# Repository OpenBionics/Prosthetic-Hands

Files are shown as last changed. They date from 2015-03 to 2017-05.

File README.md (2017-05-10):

# OpenBionics - Prosthetic Hands
 
Nowadays most prosthetic hands cost dozens of thousands of USD. The OpenBionics initiative (www.openbionics.org) presents a new open-source design for highly functional prosthetic hands. The proposed hands cost less than 200$, weigh less than 300 gr and can be easily fabricated with off-the-shelf materials and rapid prototyping techniques (3D Printing). 

A novel differential mechanism (based on the whiffletree) allows the user to block the motion of each finger independently and facilitates the execution of 144 different grasps with only 1 actuator. The design is based on parametric models of hand anthropometry studies, so it can easily be personalized to specific patients.

## Contents

In this repository you can find:
* Detailed assembly guide for the replication of OpenBionics prosthetic hand 
* Parametric CAD files for personalized design
  * 2D CAD design files for laser cutter 
  * 3D CAD design files for 3D printer
* Breakout board 
* Prosthetic hand kinematics in MATLAB using robotics toolbox
* Arduino software for HerkuleX DRS-0201 servo motor operation
* Archive of various images

## Notes

Please open a [GitHub issue](https://github.com/OpenBionics/Prosthetic-Hands/issues) if you encounter any problem.

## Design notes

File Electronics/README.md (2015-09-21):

# Electronic Breakout Board for Prosthetic Hand

We present the development of a breakout board for controlling our prosthetic hand. It is a PCB (printed circuit board) with pin headers to accomodate two different servo motors, such as standard servo and herkulex. It can have both analog inputs (e.g. [EMG](http://www.advancertechnologies.com/p/muscle-sensor-v3.html) signals) and digital inputs (e.g. buttons for [RobotHandExtension](https://github.com/OpenBionics/Robot-Hands/tree/master/CAD/Interfaces/Extension)).
An I2C bus can also be used in order to connect sensors like [takktile] (http://www.takktile.com/) or other servos such as the [openservo](http://openservo.com/). The breakout board also has external pins for development. 

The main microcontroller we currently use is an Arduino Micro Pro, equipped with an ATmega32U4 core. The PCB can be powered by an external power supply or a battery. 

The board is currently under testing. Pictures of the board and its development process can be found below.

# Pinout

The Pin Mapping of the breakout board.

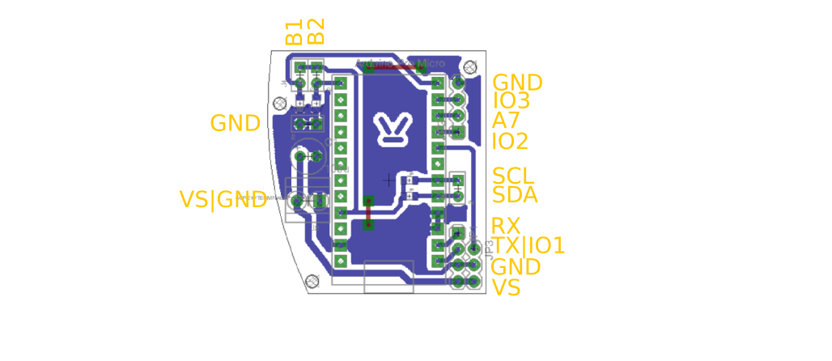
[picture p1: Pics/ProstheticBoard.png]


# Board Development

The development of the breakout board was done using the facilities of
the Athens Hackerspace (Thanks!!!). Some photos of the development process and 
final result.

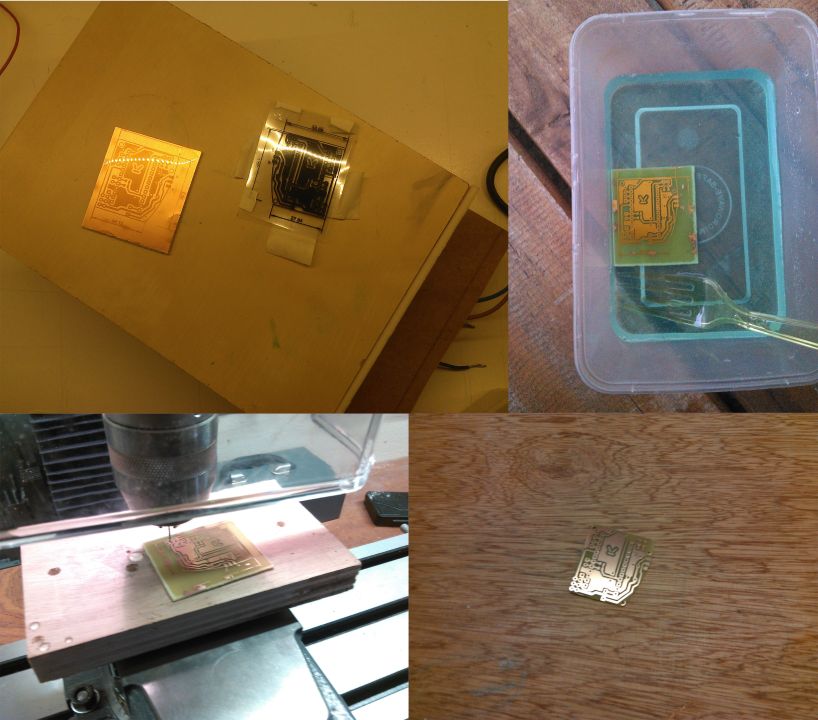
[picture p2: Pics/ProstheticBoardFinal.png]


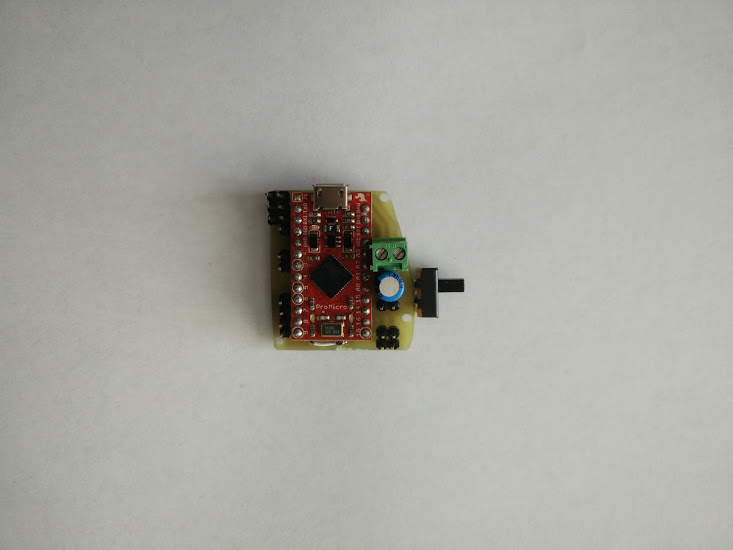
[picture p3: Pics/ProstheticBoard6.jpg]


The OpenBionics Electronics Library can be found [here](https://github.com/OpenBionics/Robot-Hands/tree/master/Electronics).

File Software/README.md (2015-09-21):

# Arduino Firmware

In order to evaluate the capabilities of our prosthetic hand, we developed a simple firmware for Arduino using this [library](http://robottini.altervista.org/dongbu-herkulex-arduino-library-2) for Herkulex DRS-0201. 

We modified the library in order to control the motor with an [Arduino](https://www.arduino.cc) Micro Pro.

# Next Steps

We plan on controlling our prosthetic hands with different interfaces, such as [these](https://github.com/OpenBionics/Robot-Hands/tree/master/CAD/Interfaces) or EMG sensors. 

A schematic depicting the high-level control architecture of our prosthetic hands can be found below.

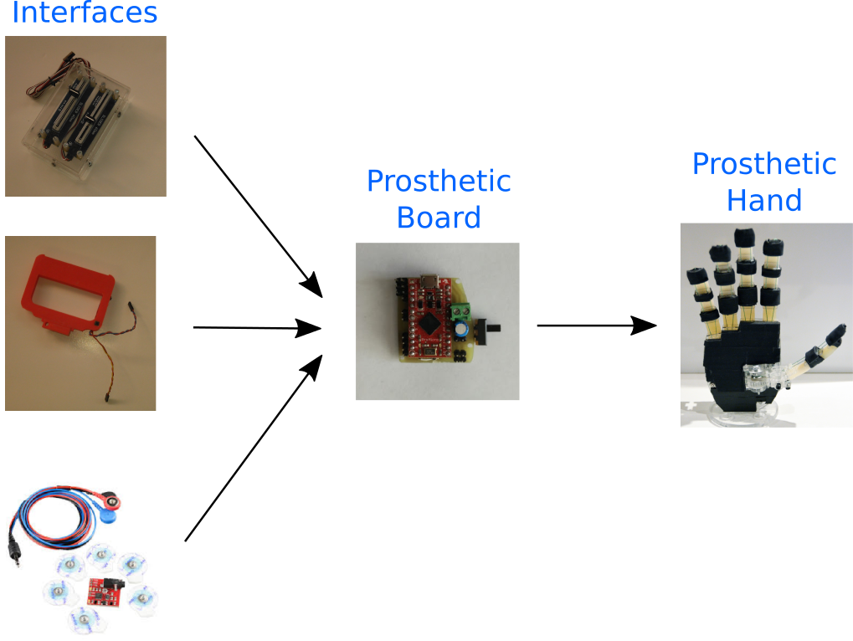
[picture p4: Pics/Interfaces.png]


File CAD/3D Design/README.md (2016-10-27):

# Parametric CAD file for 2D Design

## Guide for personalized design

Τhe use of parametric models derived from human hand anthropometry studies, allows for the development of personalized prostheses. The only parameters that we need in order to derive the finger phalanges lengths and the personalized finger base frames positions and orientations, are the human hand length (HL) and the human hand breadth (HB). 

We have modified our CAD files in order to integrate the required parameters (HL & HB) for the replication of a personalized design. Firstly, you need to decide which hand you want to replicate (Right or Left). You can find below a quick guide for the production of the personalized design. The procedure is the same for both hands.

1. Open the part file "prostheticParameters.SLDPRT" which can be found @ <a href="https://github.com/OpenBionics/Prosthetic-Hands/blob/master/CAD/3D%20Design/Left_hand/prostheticParameters.SLDPRT">Prosthetic-Hands/CAD/3D Design/Left_hand</a>.
2. Make the "parametersSketch" file editable. You can see there, the parameters that you can change. Their values are reported in mm and NOT in inches.
3. Open the assembly file "AnthropomorphicHandAssembly.SLDASM" which can be found @ <a href= "https://github.com/OpenBionics/Prosthetic-Hands/tree/master/CAD/3D%20Design/Left_hand/Assembly">Prosthetic-Hands/CAD/3D Design//Left_hand/Assembly</a>.
4. Go to the file "prostheticParameters.SLDPRT" and change the desired values (HL=hand length, HB=hand breadth & fingerWidth) according to the following figure and then save the file.

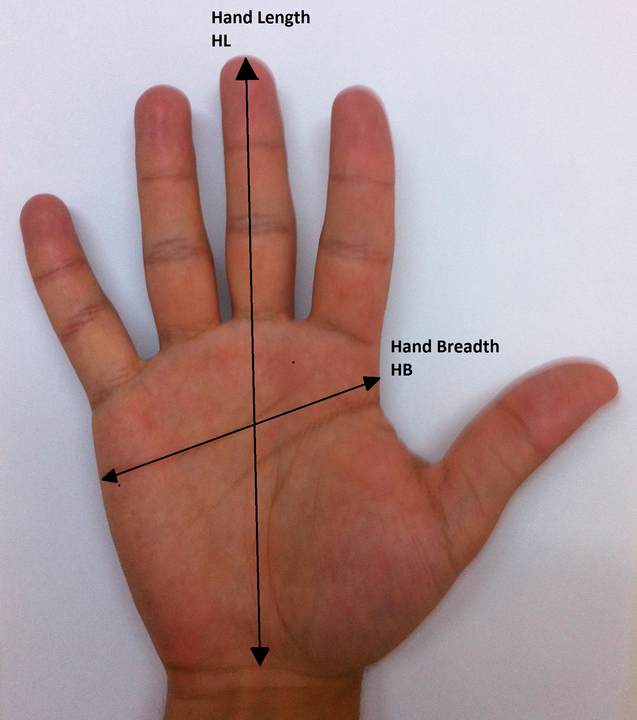
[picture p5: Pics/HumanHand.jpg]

 
5. Go to the assembly file "AnthropomorphicHandAssembly.SLDASM" and rebuild it. All .SLDPRT files that are used in the assembly should be rebuilt.
6. If you want .STL files, you should open every rebuilt part and then choose "Save as .STL".

## 3D Design Model

In the following figure you can see the 2D Design model

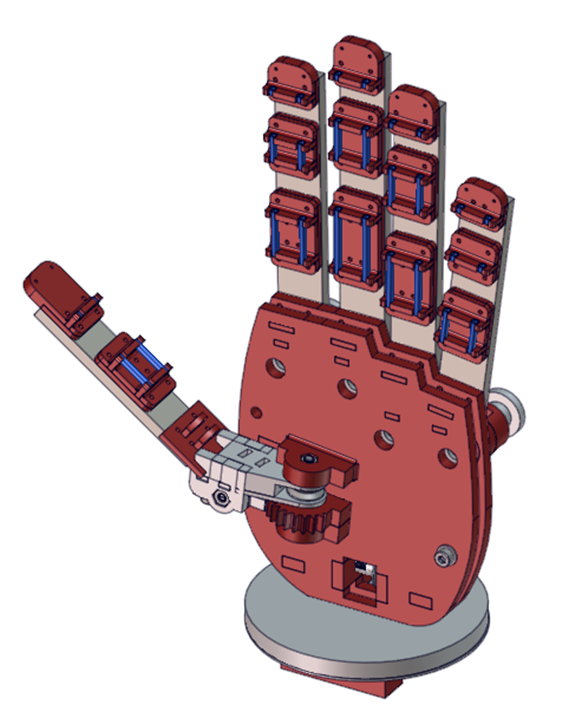
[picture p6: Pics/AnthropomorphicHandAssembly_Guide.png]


##Things to note:

1. The design has specific constraints, which cover the 95th percentile of the human hand and those are:<br/>
Hand Length: 182 - 225 mm<br/>
Hand Breadth: 82.5 - 110 mm.
2. Dimensions should be changed symmetrically. The mean HL/HB ratio is 2.2, so if your new assembly has errors it is probably either because you didn't measure correctly your hand values or because your hand construction is very far from the human mean value. 
3. For editing our CAD files you should own Solidworks 2014 or a later version. In case that you don't have the required software, complete this <a href="http://www.openbionics.org/personalizeddesignswebform/">webform</a> in the <a href="http://www.openbionics.org/">OpenBionics</a> website. We are currently in the process of preparing our designs with open-source CAD software. 
4. Our approach is inspired by the Yale Open Hand project. More details can be found <a href="http://www.eng.yale.edu/grablab/openhand/OpenHand%20CAD%20Guide.pdf">here<a/>.

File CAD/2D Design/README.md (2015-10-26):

# Parametric CAD file for 2D Design

## Guide for perosnaliszd design

Τhe use of parametric models derived from human hand anthropometry studies, allows for the development of personalized prostheses. The only parameters that we need in order to derive the finger phalanges lengths and the personalized finger base frames positions and orientations, are the human hand length (HL) and the human hand breadth (HB). 

We have modified our CAD files in order to integrate the required parameters (HL & HB) for the replication of a personalized design. Firstly, you need to decide which hand you want to replicate (Right or Left). You can find below a quick guide for the production of the personalized design. The procedure is the same for both hands.

1. Open the part file "prostheticParameters.SLDPRT" which can be found @ <a href="https://github.com/OpenBionics/Prosthetic-Hands/tree/master/CAD/2D%20Design/LeftHand">Prosthetic-Hands/CAD/2D Design/Left</a>.
2. Make the "parametersSketch" file editable. You can see there, the parameters that you can change. Their values are reported in mm and NOT in inches.
3. Open the assembly file "AnthropomorphicHandAssembly.SLDASM" which can be found @ <a href= "https://github.com/OpenBionics/Prosthetic-Hands/tree/master/CAD/2D%20Design/LeftHand/Assembly">Prosthetic-Hands/CAD/2D Design/Left/Assembly</a>.
4. Go to the file "prostheticParameters.SLDPRT" and change the desired values (HL=hand length, HB=hand breadth & fingerWidth) according to the following figure and then save the file.


 
5. Go to the assembly file "AnthropomorphicHandAssembly.SLDASM" and rebuild it. All .SLDPRT files that are used in the assembly should be rebuilt.
6. If you want .STL files, you should open every rebuilt part and then choose "Save as .STL".

## 2D Design Model

In the following figure you can see the 2D Design model

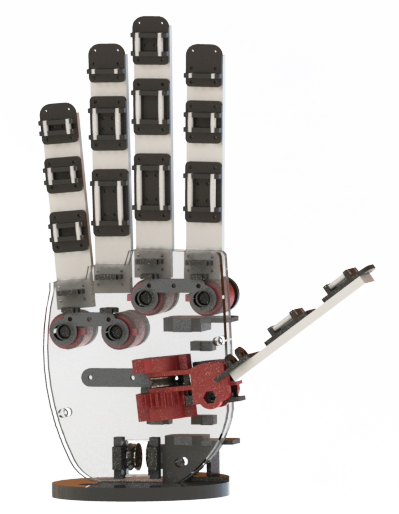
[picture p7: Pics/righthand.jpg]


## Things to note:

1. The design has specific constraints, which cover the 95th percentile of the human hand and those are:<br/>
Hand Length: 182 - 225 mm<br/>
Hand Breadth: 82.5 - 110 mm.
2. Dimensions should be changed symmetrically. The mean HL/HB ratio is 2.2, so if your new assembly has errors it is probably either because you didn't measure correctly your hand values or because your hand construction is very far from the human mean value. 
3. For editing our CAD files you should own Solidworks 2014 or a later version. In case that you don't have the required software, complete this <a href="http://www.openbionics.org/personalizeddesignswebform/">webform</a> in the <a href="http://www.openbionics.org/">OpenBionics</a> website. We are currently in the process of preparing our designs with open-source CAD software. 
4. Our approach is inspired by the Yale Open Hand project. More details can be found <a href="http://www.eng.yale.edu/grablab/openhand/OpenHand%20CAD%20Guide.pdf">here<a/>.

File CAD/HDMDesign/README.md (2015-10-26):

# New HDM Design of Robot Fingers

## Introduction

Our initial method of creating fingers for robot and prosthetic hands was very simple and it didn't require any complex tools (silicone sheets were stitched onto the rigid phalanges with simple needles). The main disadvantages of this method are:
* the process isn't automated,
* the aesthetic aspect of the finger is not optimal (i.e., it doesn't feel like a product),
* the finger cannot easily accommodate extra parts (e.g., sensing elements or other electronics).

For these reasons we searched different fabrication methods for developing hands based on flexure joints.

Recently Ma et al [1] proposed a new methodology that is called hybrid deposition manufacturing [HDM](http://www.eng.yale.edu/grablab/pubs/Ma_JMR2015.pdf). HDM combines additive manufacturing (AM) with multi-material deposition and embedded components in order to produce robotic, mechatronic, and other articulated mechanisms.

## Design

Using the HDM approach for our prosthetic fingers we can embed inside them a wide range of electronics, like force sensors, flex sensors or even NFC tags that will facilitate interactions with other electronic devices. Of course the new design has the disadvantage that it requires more complex tools and is slightly more expensive.

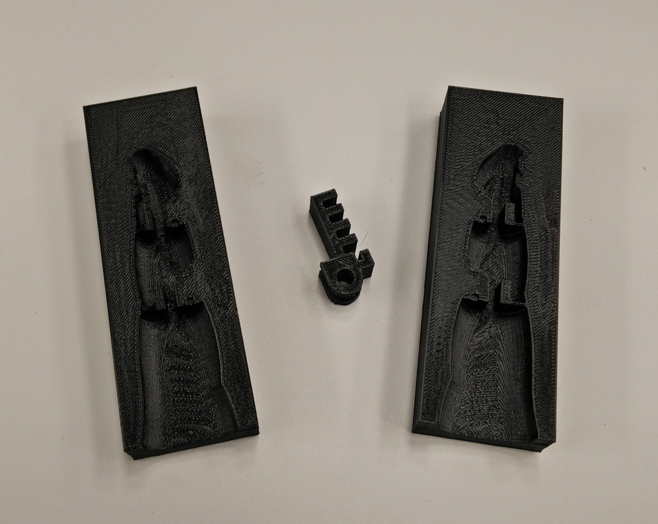
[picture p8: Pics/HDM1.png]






The proposed design can be based on the human hand model. For now we use a ready [model](https://grabcad.com/library/human-left-hand) in SolidWorks. In the future we plan to use a 3D scanner (e.g., kinect, project soli, etc.) to reconstruct the intact hand of amputee, derive the mirror hand and build a personalized prosthesis.

To use this new design in SolidWorks, you can download the files form [here](https://grabcad.com/library/human-left-hand). When you open the .sldASM files, SolidWorks will ask for the missing parts. These parts can be found in the following [3D model](https://grabcad.com/library/human-left-hand). A future direction of ours is to make the HDM design parametric and migrate it to FreeCAD, as we did for the [initial design](https://hackaday.io/project/4745-openbionics-affordable-prosthetic-hands/log/27049-prosthetic-hand-in-freecad-palm-and-tendon-routing).

## Materials and Tools Required

As depicted the build of materials are:

* paint of the desired color
* liquid polyurethane (PMC 780)
* cotton swabs
* paper tape
* NFC tags

The necessary tools are:

* a weighting scale
* a vacuum chamber
* plastic cups to mix the two liquid silicone parts.

The prices of the different hand components can be found [here](https://hackaday.io/project/4745-openbionics-affordable-prosthetic-hands/log/27133-the-role-of-the-openbionics-project-in-a-world-of-overprized-prosthetic-devices). The NFC tags [cost](http://www.amazon.com/gp/product/B00MNYCIKG?psc=1&redirect=true&ref_=oh_aui_detailpage_o00_s00) 15.50$ (for 25 tags). 



## More Details

More details about this design can be found [here](https://hackaday.io/project/4745/logs?page=2).

### References

[1] Raymond R. Ma, Joseph T. Belter and Aaron M. Dollar, "Hybrid Deposition Manufacturing: Design Strategies for Multi-Material Mechanisms via 3D-Printing and Material Deposition", Journal of Mechanisms and Robotics, 2015.

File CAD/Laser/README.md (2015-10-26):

# Laser Cutter files

These files should be imported to a laser cutter to build the 2D Design Hand.

## Building

For the version created with the laser cutter, we used Plexiglas (acrylic) because it is low-cost, light-weight, it can be easily found, it has good durability, significant ultimate tensile strength (8.500 - 11.250 psi) and almost the same density (1.19 gr / cubic cm | 0.043 lbs / cubic inch), with other common plastics like ABS. The laser cutting machine used, was the Universal Laser Systems VSL 3.5 that appears in the following image. The estimated fabrication time with the laser cutter is ~ 2 hrs.

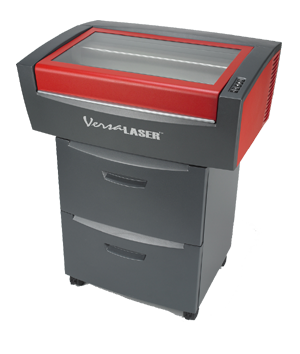
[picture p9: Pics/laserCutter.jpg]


The Prosthetic Hand with laser cutting parts appears in the following image.

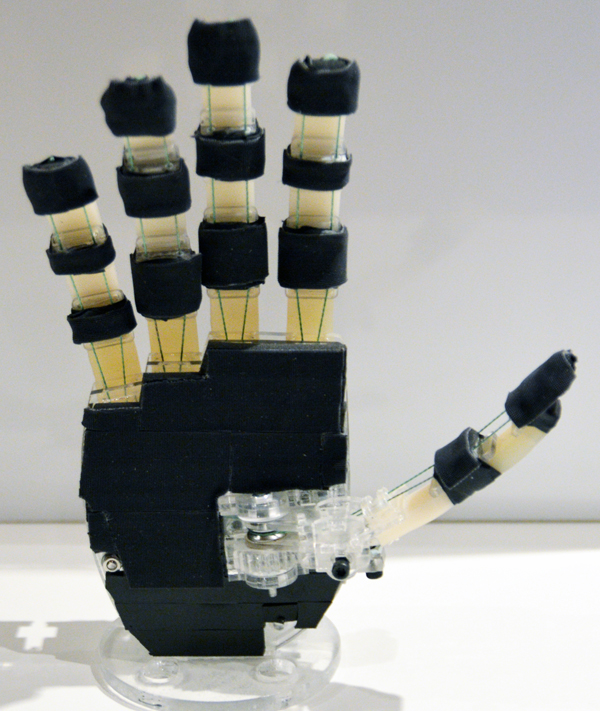
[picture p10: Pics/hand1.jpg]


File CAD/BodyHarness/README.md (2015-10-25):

# Α Body Powered Actuation System for Prosthetic Hands

## The Idea

An old and reliable method of controlling prosthetic devices is by using a harness-socket actuation system in a body powered manner [1]. In order to further reduce the cost of our prosthetic hands omitting any kind of electronics and servos, we designed a body powered actuation system that an amputee can use as an interface to control a prosthetic hand. The proposed system is inspired by the classic harness-socket actuation systems but is designed as an exosceleton. The system consists of modular parts. Depending on the user's arm length an appropriate number of intermediate modules can be printed together with the end-effector and the tendon routing entry part.

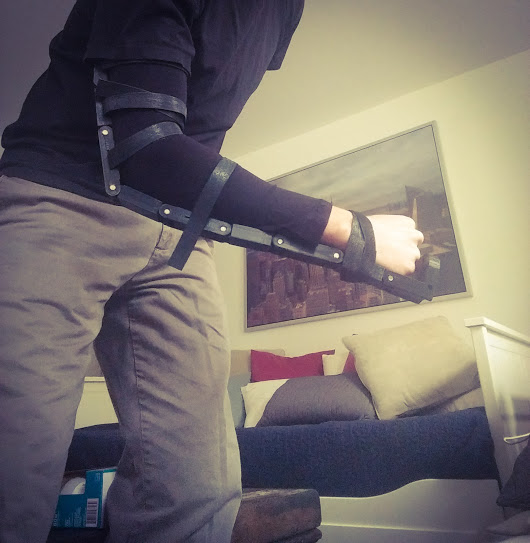
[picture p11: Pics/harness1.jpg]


## Description

The proposed body powered actuation system, consists of:
* modular 3D-printed parts 
* pins, dowels or shafts
* velcro tape
* an elastic arm sleeve
* dyneema thread

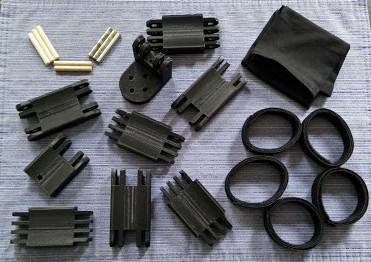
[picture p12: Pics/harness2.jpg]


The mechanism can be replicated and assembled quite easily, as depicted in the picture below. Moreover, the proposed system with a prosthetic hand attached at the end-effector, can be used as a body powered prosthesis simulator for non-amputees that want to experience how functional a prosthesis is (e.g., kin that want to experience what amputees - family members feel). The cost of the system is less than 25$ and the weight 250 gr. Enjoy! 

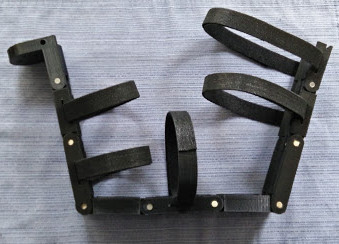
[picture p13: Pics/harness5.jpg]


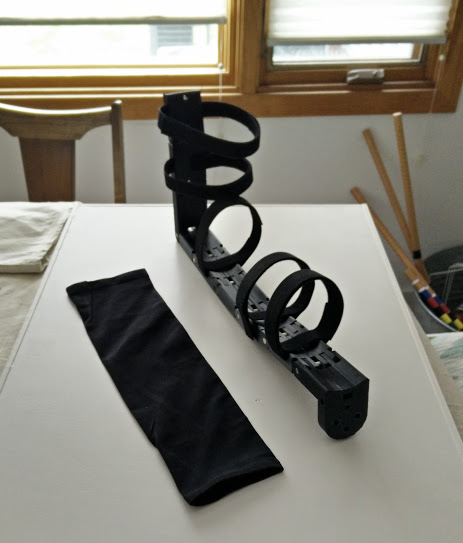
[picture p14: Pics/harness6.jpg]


**References:** 

[1] R. J. Pursley, "Harness patterns for upper-extremity prostheses", Artif Limbs, 2(3):26-60, Sep 1955.

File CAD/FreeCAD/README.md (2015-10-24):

# Prosthetic Hand in Freecad

As we have already mentioned [here](https://hackaday.io/project/4745-openbionics-affordable-prosthetic-hands/log/25696-migrating-our-designs-to-freecad), we are in the process of migrating our designs to Freecad in order to be freely accessible to all and because we believe in fully open source solutions!

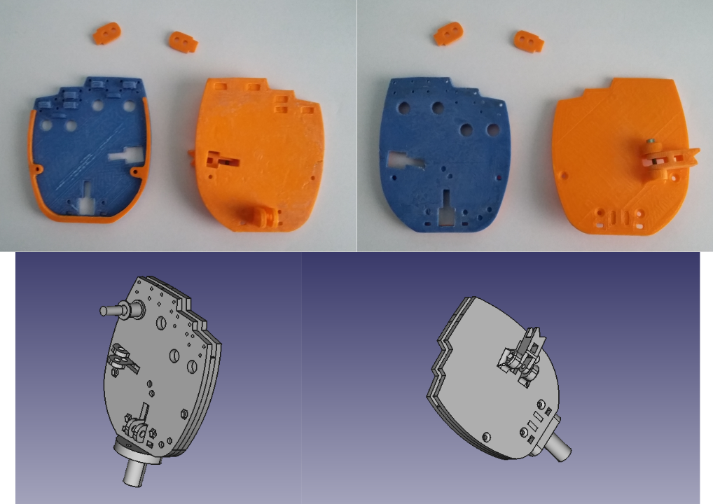
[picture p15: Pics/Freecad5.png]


Up to now we have designed the palm with the differential and the thumb abduction / adduction mechanisms. Prosthetic fingers (the easy part) will follow as we are in the process of improving their design. We have also redesigned some parts for better performance (e.g., the bars of the differential mechanism are changed).

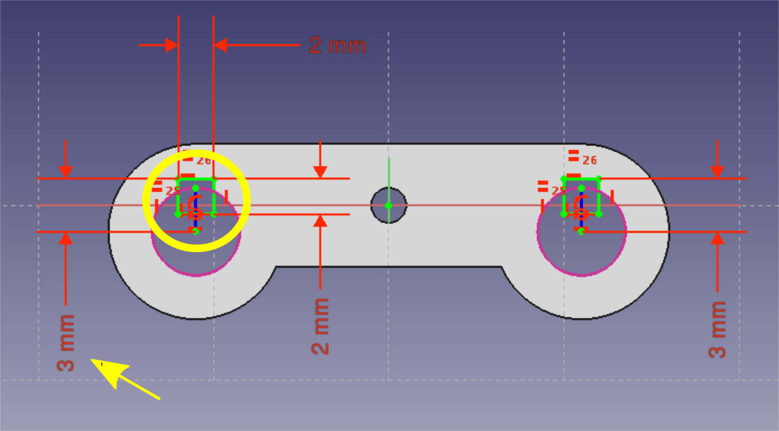
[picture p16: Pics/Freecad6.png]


As depicted, we reduced the radius of the button axle and the radius of the holes of the bars. This change, makes the coupled fingers (e.g., index and middle) more independent when one of them is locked. The radius is now 3mm. When one finger is locked and the other moves, the locked finger tendon will move a distance of 3 mm*angle_of_bar. For example, if the angle_of_bar = PI/4 then the tendon moves a distance of ~2.35 mm. 

We also modified the tendon routing. As you can see in the picture below the tendon comes out from the side of palm in order to be connected with the body harness for body powered prosthetic hands. With this configuration you can also put the servo motor in the same position (currently under development).

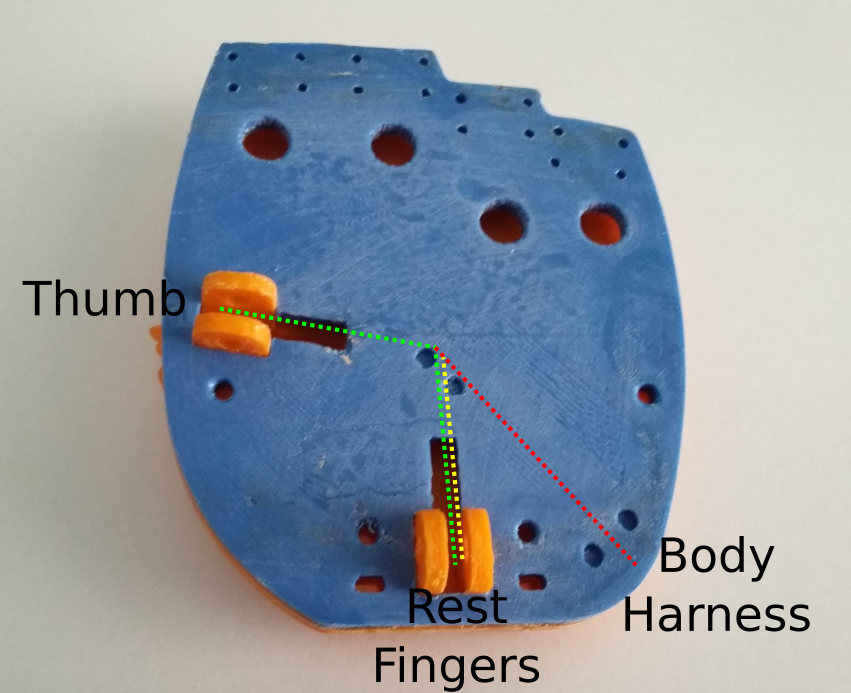
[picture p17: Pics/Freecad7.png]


A new thumb mechanism was also tested. As depicted in the picture below, we tried to add friction with a rubber layer (blue arrow) that needs appropriate tuning in order to resist the force of the tendon.

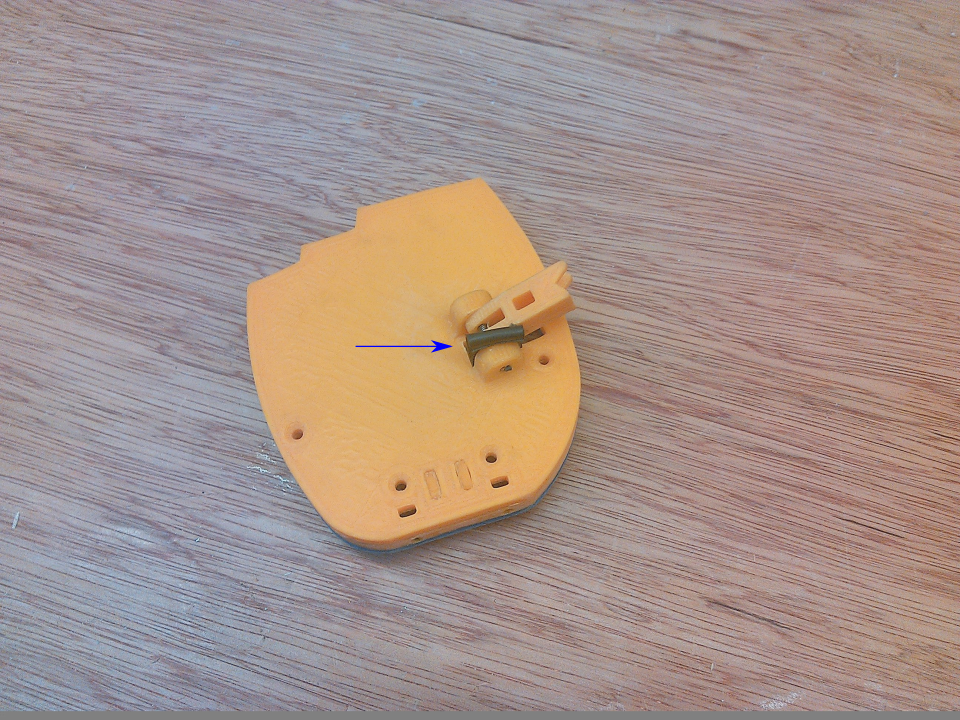
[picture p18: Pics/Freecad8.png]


Stay tuned for more updates!!!

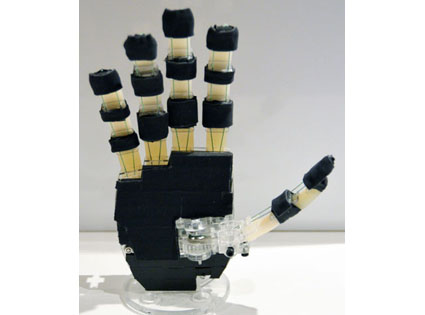
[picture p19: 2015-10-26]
Assembly Guide/tex/figures/paper_images/hand1_small.jpg

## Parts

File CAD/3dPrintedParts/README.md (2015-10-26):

# 3D Printed Parts

These parts should be printed to build the 3D Design Hand.

## Building

For the 3D printed version we used ABS and more precisely red and white 3 mm filaments with the Lulzbot TAZ 4, 3D Printer that appears in the following image. The estimated fabrication time with the 3D printer is ~ 6 hrs.

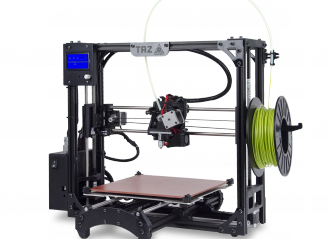
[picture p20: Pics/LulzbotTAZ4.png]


The Prosthetic Hand with 3D printed parts appears in the following image.

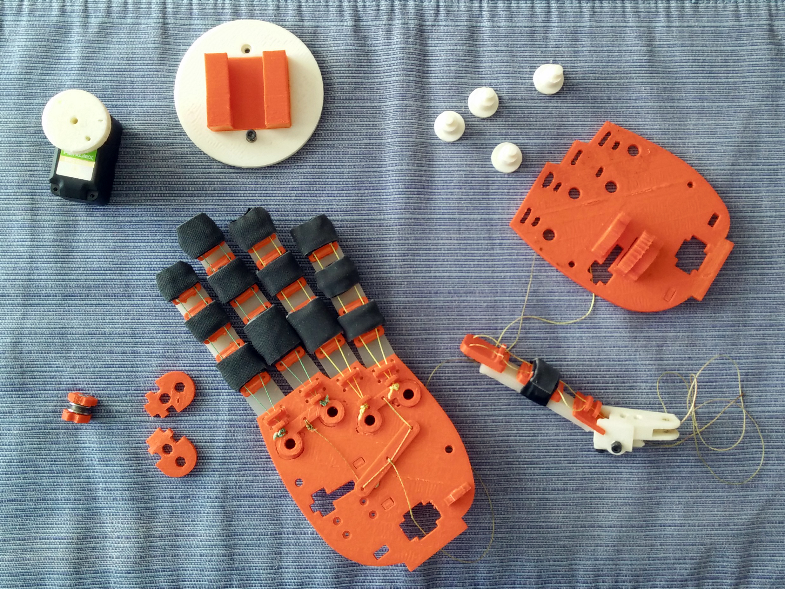
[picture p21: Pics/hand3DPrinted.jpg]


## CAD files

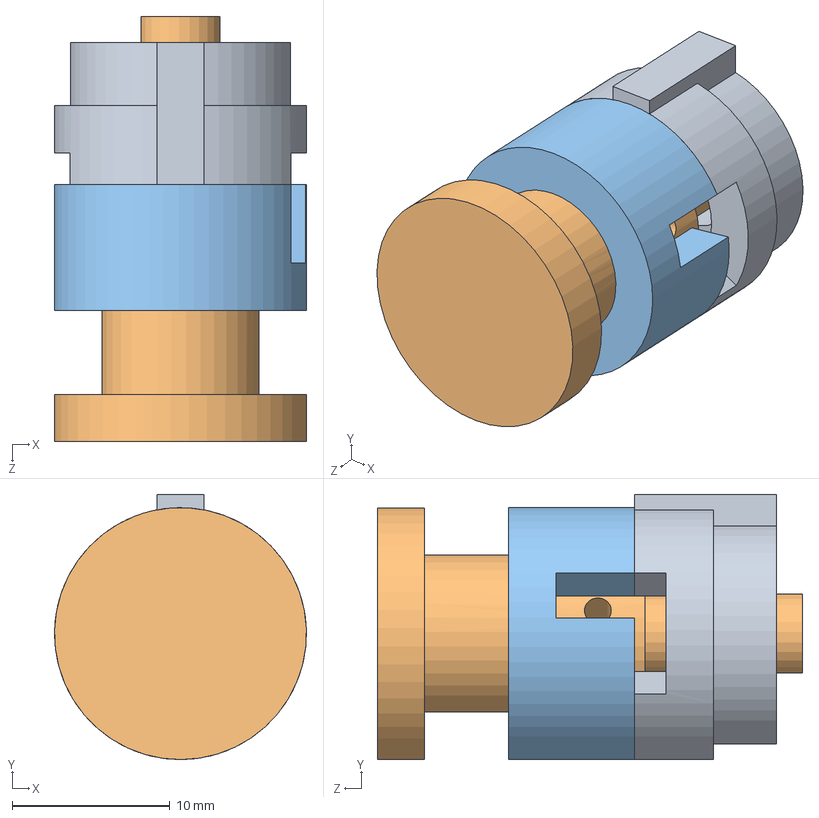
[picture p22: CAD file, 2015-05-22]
CAD/2D Design/LeftHand/Button/src/Button.SLDASM
16.0 x 16.8 x 27.0 mm
buttonBase
buttonAxle
buttonFrame

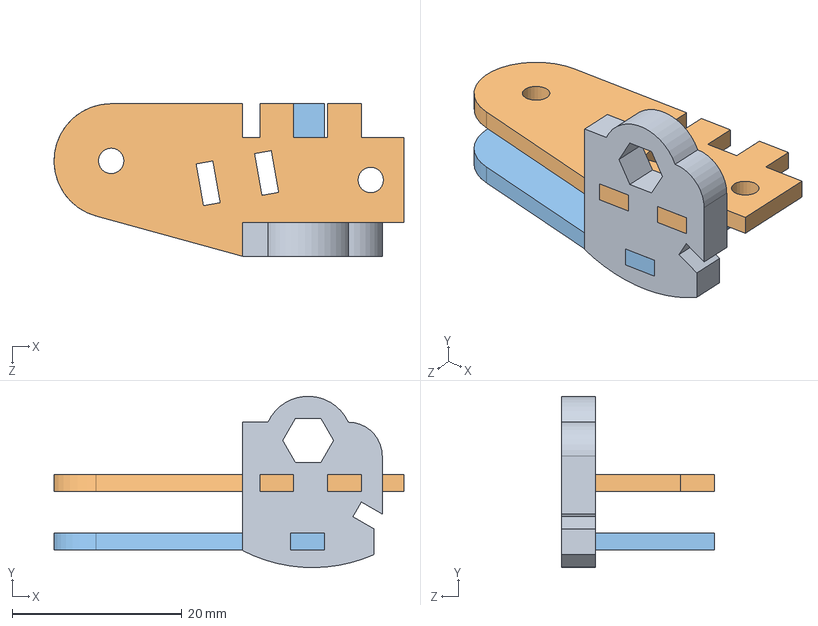
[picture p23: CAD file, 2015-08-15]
CAD/2D Design/LeftHand/Thumb_mechanism/src/thumbMovingMechanism.SLDASM
41.3 x 20.2 x 18.0 mm
thumbMovingBracket
thumbMovingBracketDown
thumbMovingBracketUp

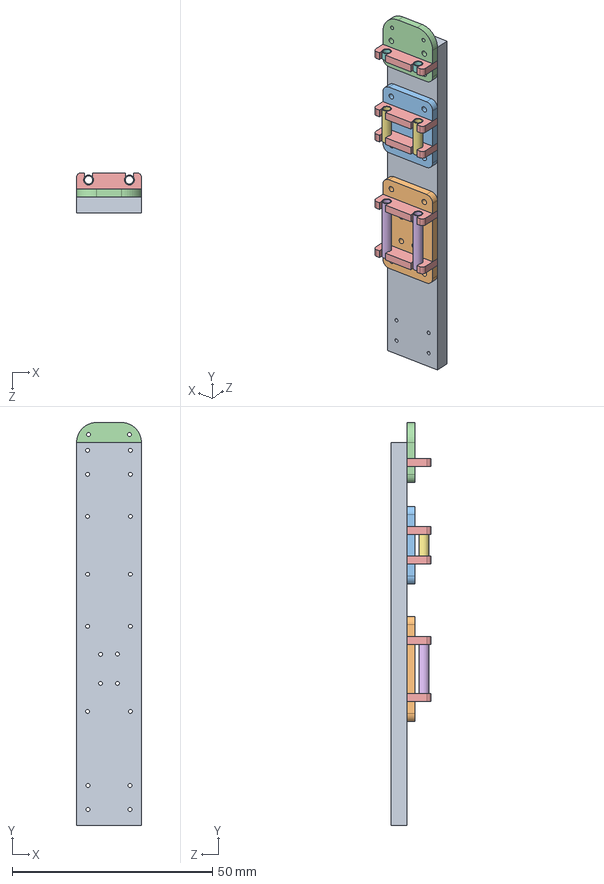
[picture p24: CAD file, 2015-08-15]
CAD/2D Design/RightHand/Fingers/src/Index/index.SLDASM
16.2 x 100.7 x 10.0 mm
indexElastomer
indexPIP
indexMIP
indexDIP
tubeDriver x 5
indexTube1 x 2
indexTube2 x 2
commonFingersTube x 2

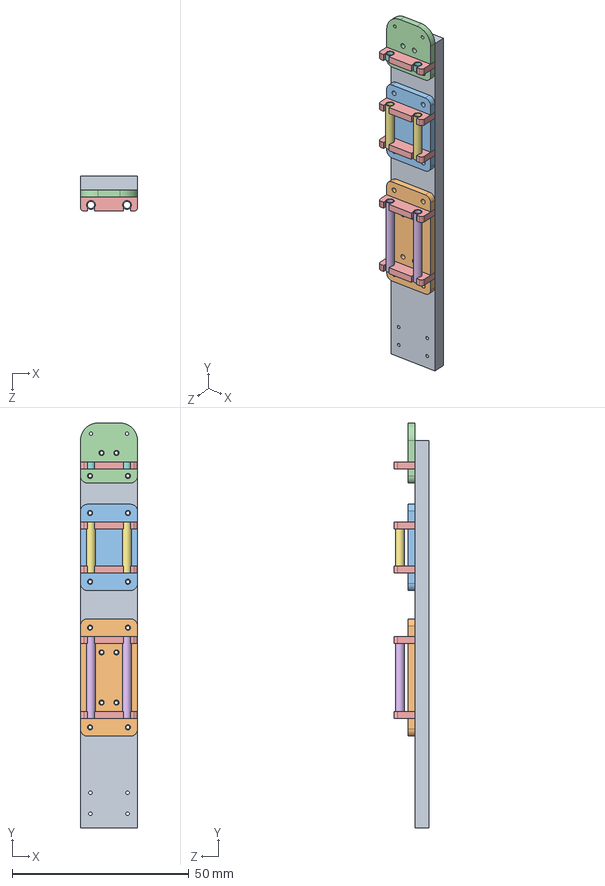
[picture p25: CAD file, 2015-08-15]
CAD/2D Design/RightHand/Fingers/src/Middle/middle.SLDASM
16.2 x 114.6 x 10.0 mm
middleElastomer
middlePIP
middleMIP
middleDIP
tubeDriver x 5
middleTube1 x 2
middleTube2 x 2
commonFingersTube x 2

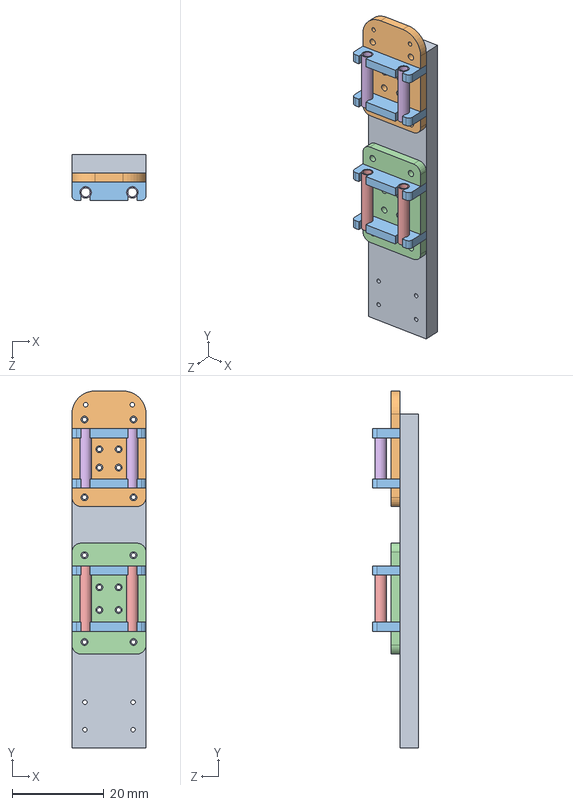
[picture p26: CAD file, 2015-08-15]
CAD/2D Design/RightHand/Fingers/src/Thumb/thumb.SLDASM
16.2 x 78.0 x 10.0 mm
thumbElastomer
thumbDIP
tubeDriver x 4
thumbPIP
thumbTube1 x 2
thumbTube2 x 2

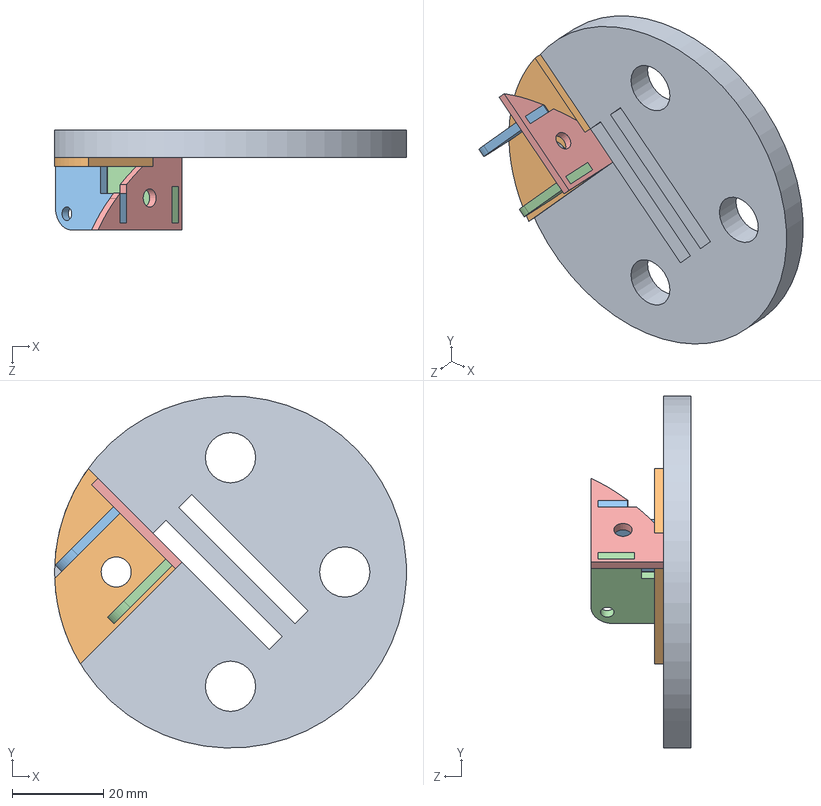
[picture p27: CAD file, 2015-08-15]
CAD/2D Design/RightHand/Flange/src/FlangeAssembly.SLDASM
77.0 x 77.0 x 21.9 mm
flange
supportHandFlange2
SupportBaseFlange1
SupportBaseFlange2
SupportHandFlange1

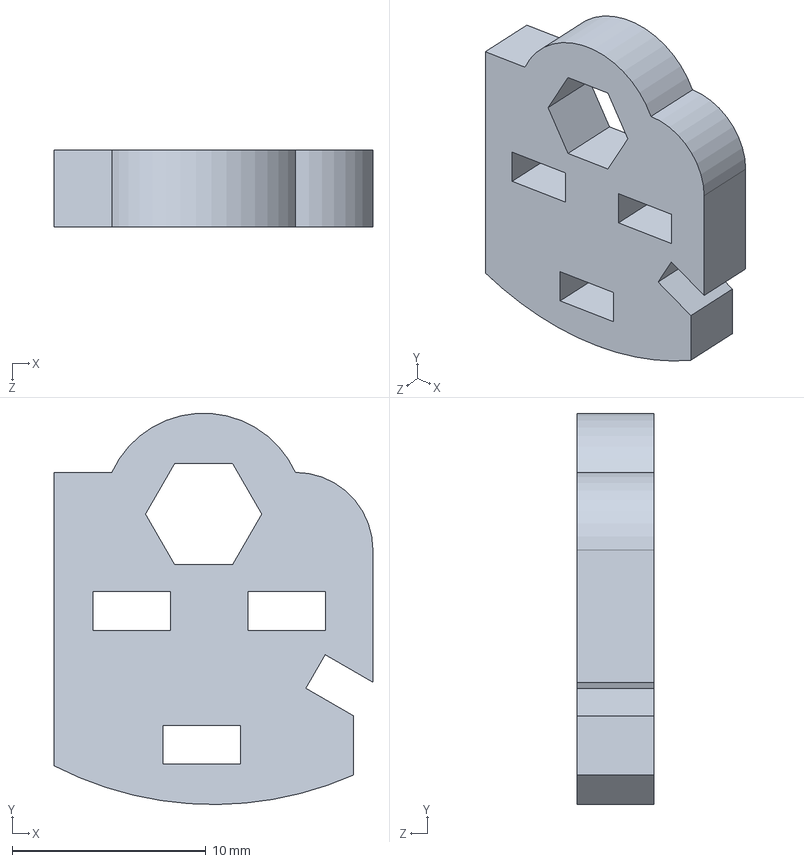
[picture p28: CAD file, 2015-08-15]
CAD/2D Design/RightHand/Thumb_mechanism/src/thumbMovingMechanism.SLDASM
16.5 x 20.2 x 4.00 mm

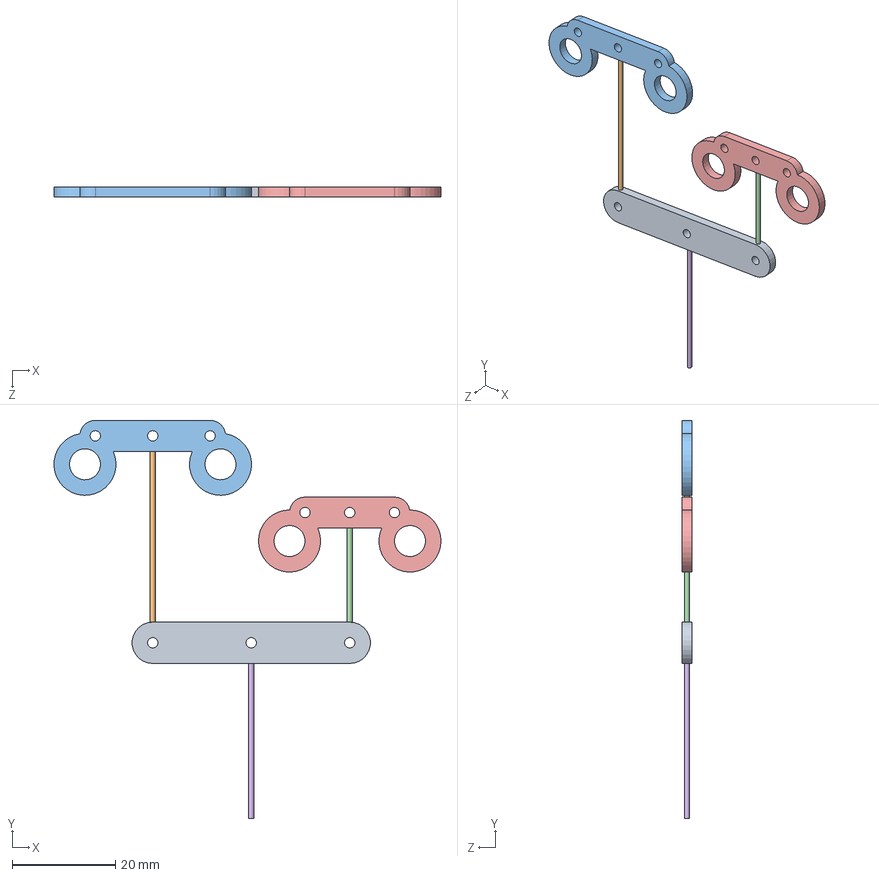
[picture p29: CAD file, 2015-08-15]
CAD/2D Design/RightHand/Whipheel_tree/src/whiffleetree.SLDASM
74.8 x 77.0 x 2.00 mm
mainBar
dynema1
barIndexMiddle
dynema2
barMiddlePinky
dynema3

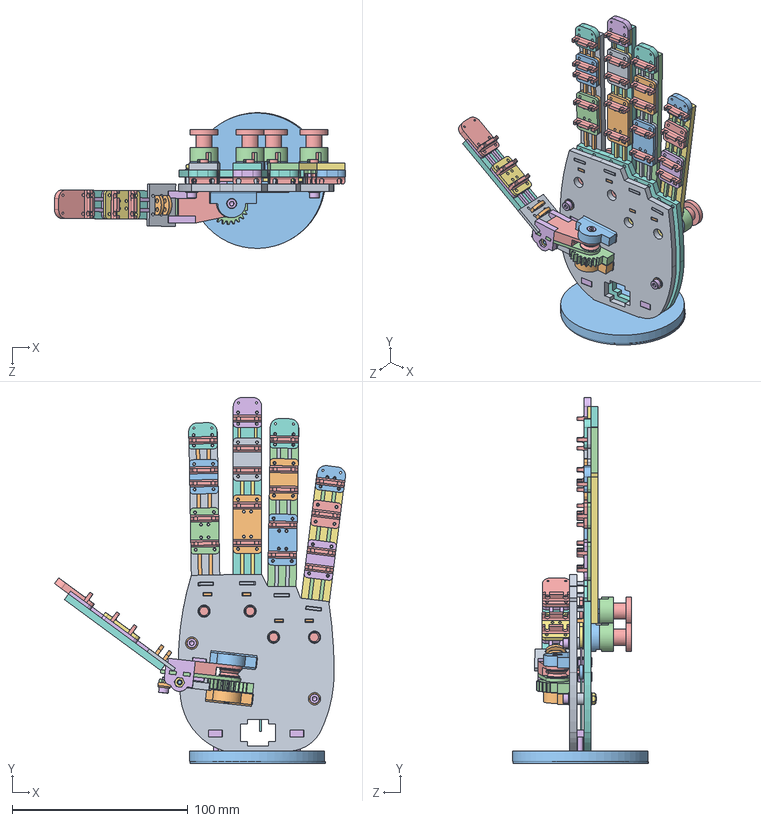
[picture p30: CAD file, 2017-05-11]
CAD/3D Design/Left_hand/Assembly/prostheticLeft.SLDASM
165.5 x 208.2 x 77.2 mm
palmDown
thumbBracket
thumbBracket1
toothedMechansimL
pulley x 2
socket head cap screw_iso x 6
hex nut style 1 gradeab_iso x 5
palmUp
driverBaseFrame1 x 4
driverBaseFrame2 x 4
buttonBase x 4
buttonFrame x 4
buttonAxle x 4
BasePulleyInsidePalm x 4
slotted set screw cup point_iso
indexDIP
indexElastomer
indexJointBase
indexMIP
indexPIP
tubeDriver x 22
middleDIP
middleJointBase
middleElastomer
middleMIP
middlePIP
pinkyDIP
pinkyJointBase
pinkyMIP
pinkyPIP
pinkyElastomer
ringDIP
ringJointBase
ringMIP
ringPIP
ringElastomer
thumbDIP
thumbJointBase
thumbPIP
thumbElastomer
thumbBase
thumbMechanismDriver x 2
mainBar
dynema1
barIndexMiddle
dynema2
barRingPinky
dynema3
spacer x 2
plain washer 10673 type snl_iso x 5
FlangePlate
thumbMovingBracketDown
thumbMovingBracketUp
thumbMovingBracket x 2
lockMechanismBracket x 2
lockMechanismSupport
toothedBlockMechanism
thumbButton
slotted set screw flat point_iso
hex thin nut gradeb_iso

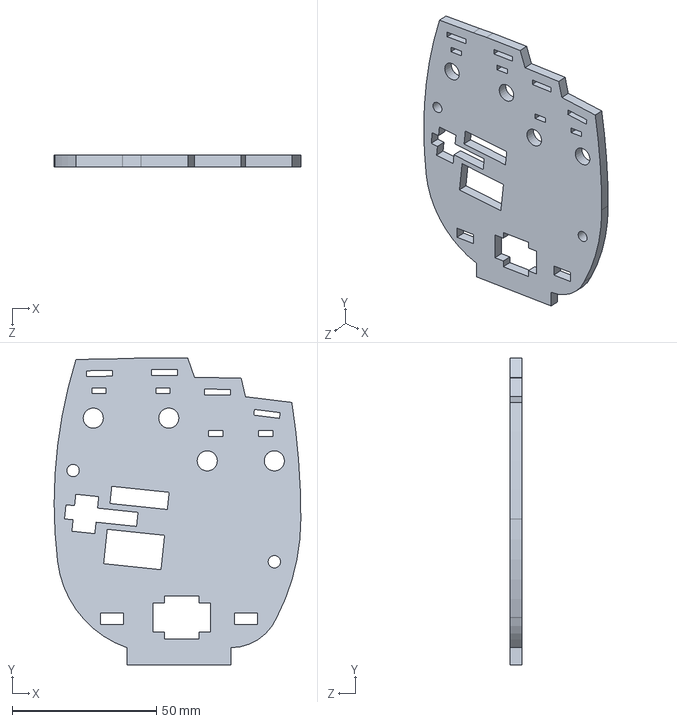
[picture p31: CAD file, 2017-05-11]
CAD/3D Design/Left_hand/Palm/src/palmDown.SLDASM
85.6 x 106.5 x 4.00 mm

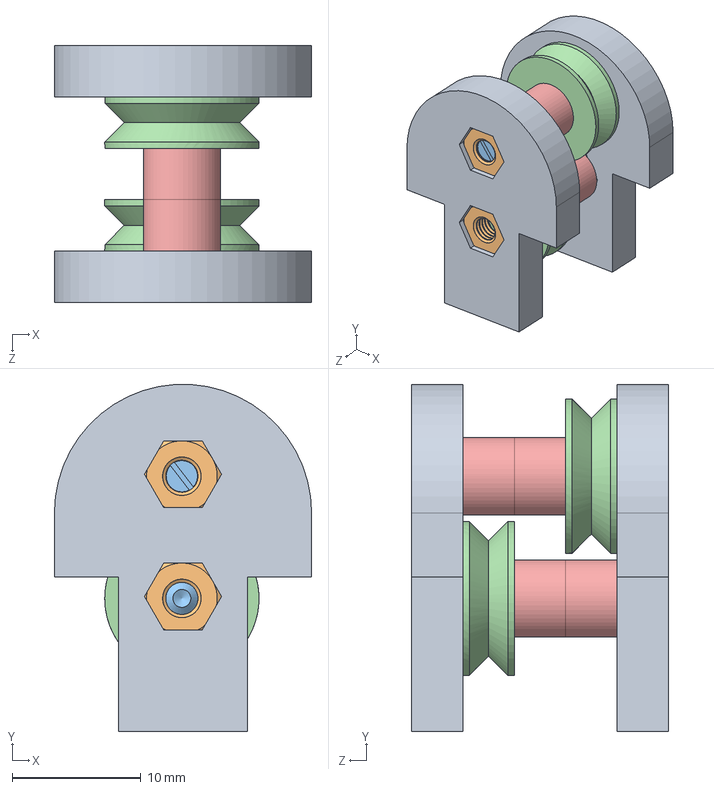
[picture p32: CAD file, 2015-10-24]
CAD/3D Design/Left_hand/ServoBase/src/Pulley/tendonRoutingLast.SLDASM
20.0 x 27.0 x 20.0 mm
supportPulley1 x 2
hex nut style 1 gradeab_din x 4
slotted set screw cup point_din x 2
pulley x 2
plasticSpacer x 4

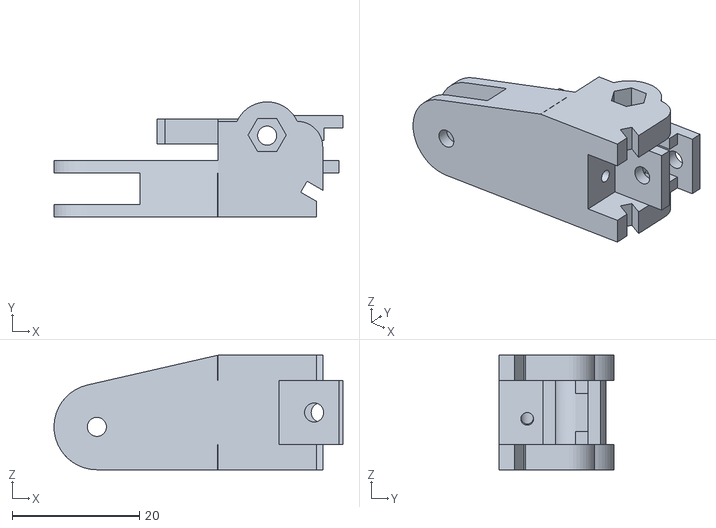
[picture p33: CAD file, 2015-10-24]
CAD/3D Design/Left_hand/Thumb_Mechanism/thumbMovingAssembly.STL
45.4 x 18.1 x 18.0

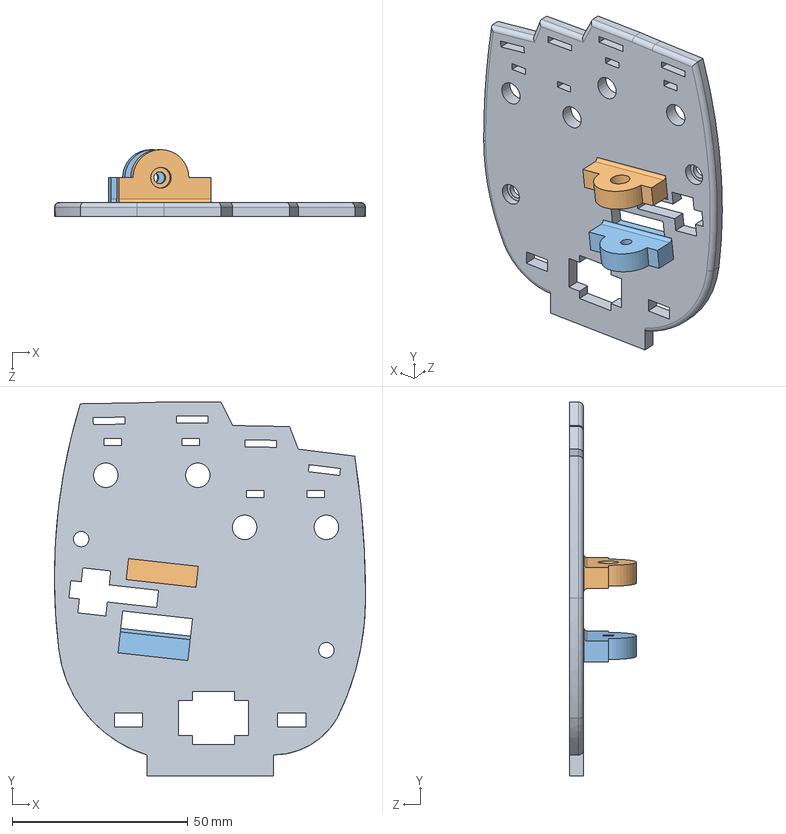
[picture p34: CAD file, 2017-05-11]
CAD/3D Design/Right_hand/Palm/src/palmDown.SLDASM
88.6 x 106.5 x 19.0 mm
palmDown
thumbBracket1
thumbBracket

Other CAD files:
CAD/2D Design/RightHand/Button/src/Button.SLDASM
CAD/3D Design/Right_hand/Assembly/prostheticRight.SLDASM
CAD/2D Design/LeftHand/Button/Button.STL
CAD/2D Design/LeftHand/Button/src/buttonAxle.SLDPRT
CAD/2D Design/LeftHand/Button/src/buttonBase.SLDPRT
CAD/2D Design/LeftHand/Button/src/buttonFrame.SLDPRT
CAD/2D Design/LeftHand/Fingers/Common Parts/driverBaseFrame1.STL
CAD/2D Design/LeftHand/Fingers/Common Parts/driverBaseFrame2.STL
CAD/2D Design/LeftHand/Fingers/Common Parts/tubeDriver.STL
CAD/2D Design/LeftHand/Fingers/Index/index.STL
CAD/2D Design/LeftHand/Fingers/Index/indexDIP.STL
CAD/2D Design/LeftHand/Fingers/Index/indexMIP.STL
CAD/2D Design/LeftHand/Fingers/Index/indexPIP.STL
CAD/2D Design/LeftHand/Fingers/Middle/middle.STL
CAD/2D Design/LeftHand/Fingers/Middle/middleDIP.STL
CAD/2D Design/LeftHand/Fingers/Middle/middleMIP.STL
CAD/2D Design/LeftHand/Fingers/Middle/middlePIP.STL
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

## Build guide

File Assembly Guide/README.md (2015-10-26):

# Assembly Guide

We present a [technical report](https://github.com/OpenBionics/Prosthetic-Hands/blob/3dPrinted/Assembly%20Guide/tex/OpenBionics_ProstheticHandsGuide2015.pdf), intended to serve as a step by step tutorial for the replication of the prosthetic hands. The guide contains illustrated instructions, carrying the user over all assembly steps and providing practical advice on any details that
require attention. 

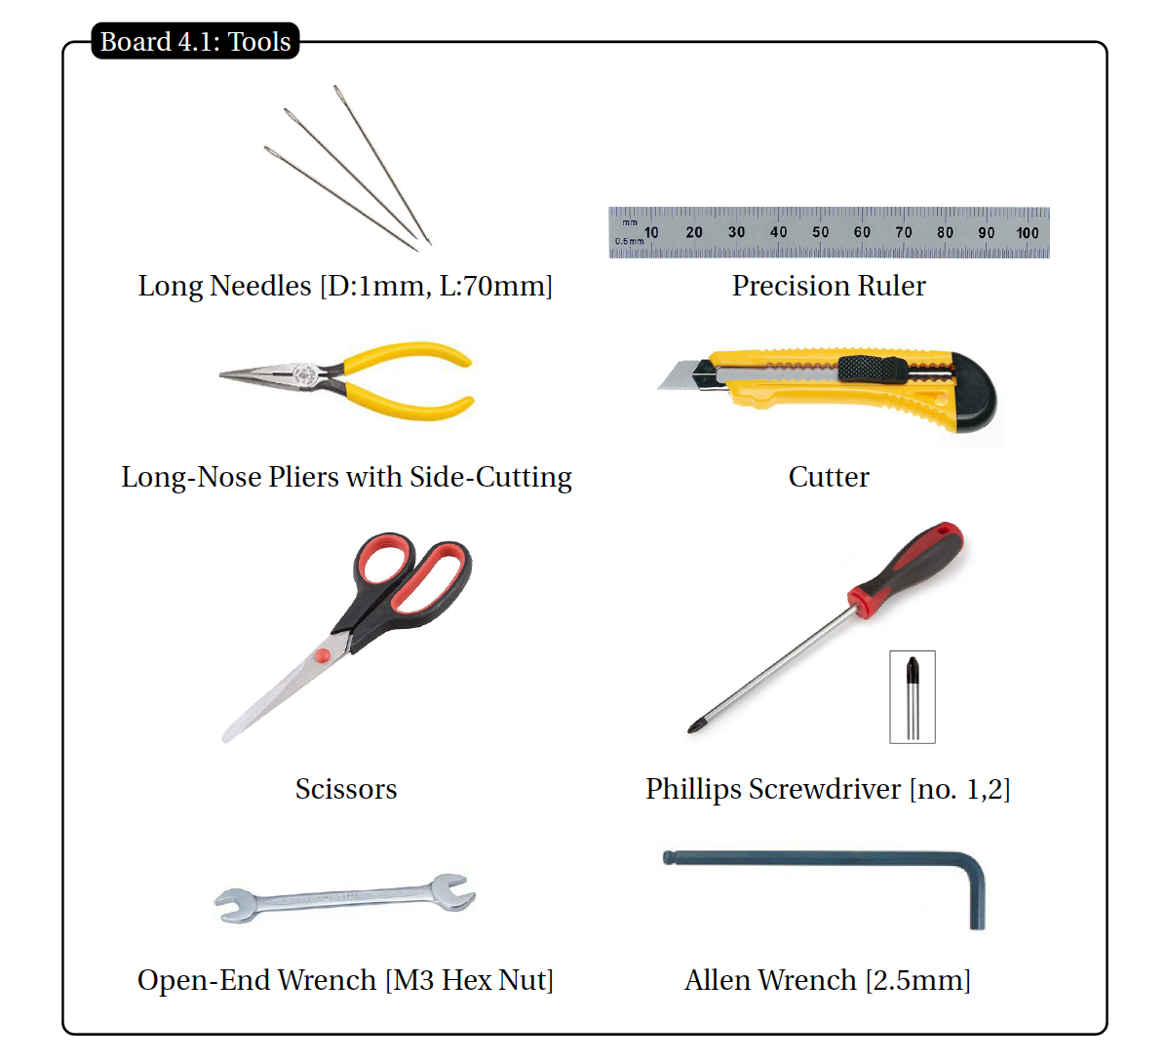
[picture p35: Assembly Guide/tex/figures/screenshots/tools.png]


Figure 1. Tools required to build all hand components.

Illustrations of all required parts, components, tools and materials (see Fig.1) are included, while comprehensive Parts Reference tables are provided (see for example a table containing all palm parts in Table 1). 

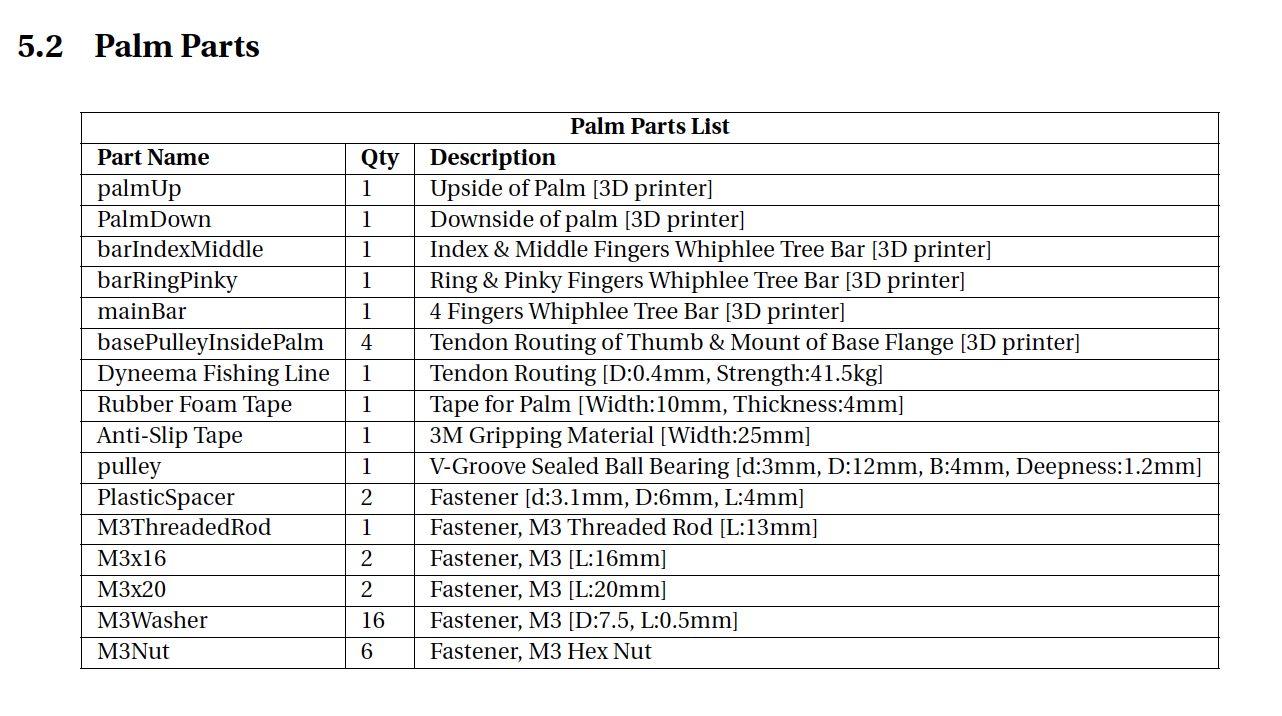
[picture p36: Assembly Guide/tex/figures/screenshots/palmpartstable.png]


Table 1. The parts required to asseble the palm.

Each assembly step is preceeded by a relevant parts list table for convenience. For example Fig. 2 contains images of all the palm parts.

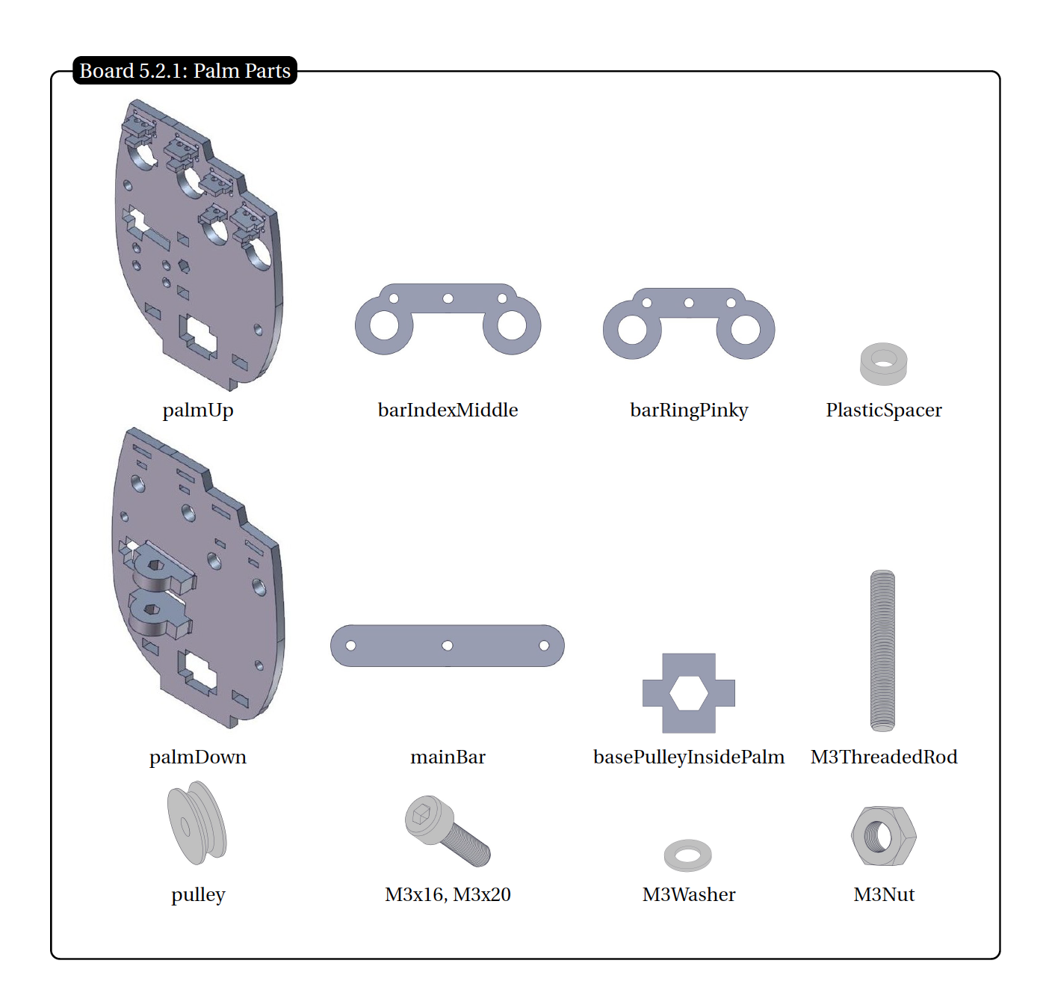
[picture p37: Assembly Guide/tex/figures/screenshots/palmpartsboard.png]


Figure 2. Parts required to build the palm.

The assembly is divided into two main sections: 1) Fingers Assembly and 2) Hand assembly, with the latter containing instructions on how to build and attach all the hand components on the palm. 

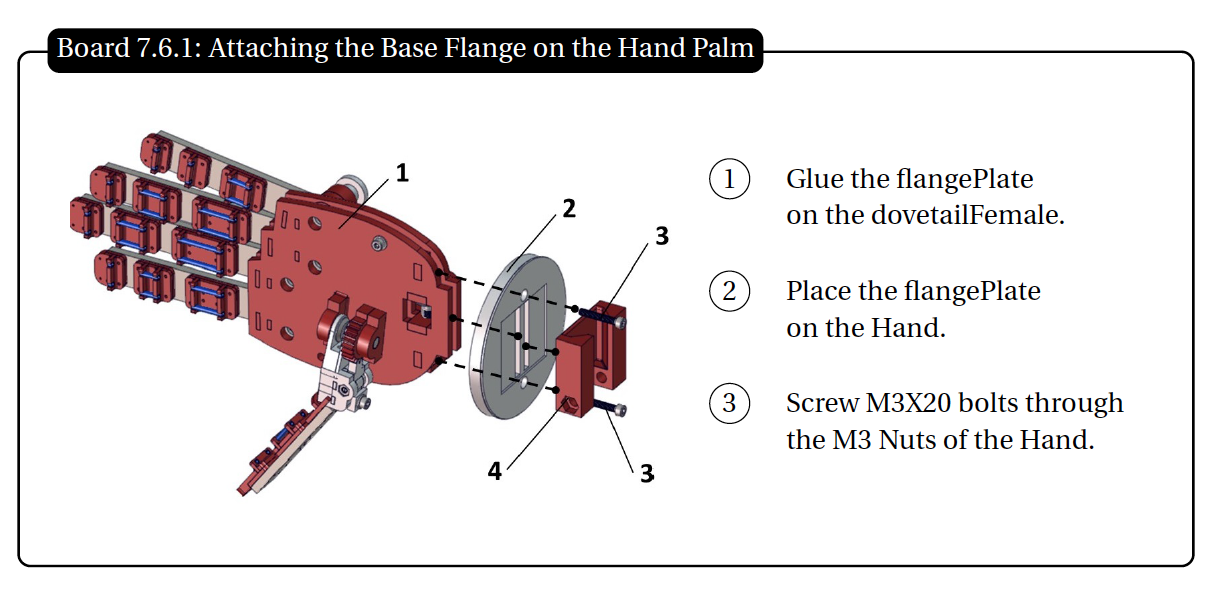
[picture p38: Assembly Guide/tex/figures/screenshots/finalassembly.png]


Figure 3. Attaching a flange on the assembled hand. 

## Hand Design

Following the design of the OpenBionics robotic hands [1], the Prosthetic hand [2] was designed to be affordable, lightweight and intrinsically-compliant. Its design is structurally and kinematically anthropomorphic. In particular, its sizing is parametrically determined by hand anthropometry studies [3], allowing for personalization and adjustment to the needs of each individual. Moreover, its kinematic model is derived by optimizing an index of anthropomorphism [4]. Finally, the prosthetic hand bears a novel differential mechanism based on the whiffletree mechanism [5] that allows the user to execute various grasping postures with a single actuator. Switching between the different postures or gestures is easy and intuitive. Simple locking buttons can independently block the motion of each finger. The proposed hands can be easily fabricated using low-cost, off-the-shelf materials and rapid prototyping techniques (e.g., 3D printing). 

## References

[1] A. Zisimatos, M. Liarokapis, C. Mavrogiannis and K. Kyriakopoulos, “Open-Source, Affordable, Light-Weight, Underactuated Robot Hands”, IEEE/RSJ International Conference on Intelligent Robots and Systems (IROS), Chicago, IL, USA, 2014.

[2] G. Kontoudis, M. Liarokapis, A. Zisimatos, C. Mavrogiannis and K. Kyriakopoulos, “Open-Source, Anthropomorphic, Underactuated Robot Hands with a Selectively Lockable Differential Mechanism: Towards Affordable Prostheses”, IEEE/RSJ International Conference on Intelligent Robots and Systems (IROS), Hamburg (Germany), 2015. 

[3] B. Buchholz, T. J. Armstrong, and S. A. Goldstein, “Anthropometric data for describing the kinematics of the human hand,” Ergonomics, vol. 35, no. 3, pp. 261–273, 1992.

[4] M. Liarokapis, P. Artemiadis, and K. Kyriakopoulos, “Quantifying Anthropomorphism of Robot Hands,” in IEEE International Conference on Robotics and Automation (ICRA), vol., no., pp.2041-2046, 6-10 May 2013.

[5] L. Birglen and C.M. Gosselin, “Force analysis of connected differential mechanisms: application to
grasping,” The International Journal of Robotics Research, vol. 25, no. 10, pp. 1033–1046, 2006.

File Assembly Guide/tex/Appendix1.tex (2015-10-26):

\section{Necessary Tools and Materials}

Our prosthetic hand can be assembled using the following tools and materials that can be easily found in hardware stores around the world.

\begin{center}
\begin{tikzpicture}
\node [mybox] (box){
	\scalebox{1.07}{
	\begin{tabular}{ c c }
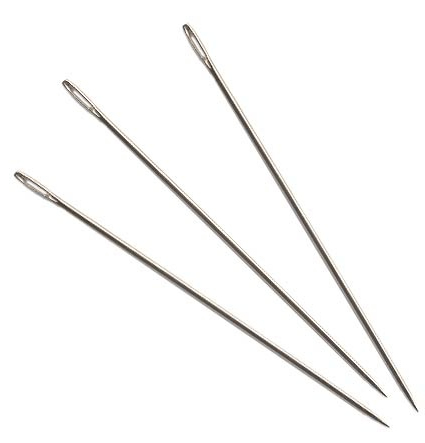
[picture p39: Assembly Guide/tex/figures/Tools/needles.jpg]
		 &
		 
		\\
		Long Needles [D:1mm, L:70mm] & Precision Ruler
		\\
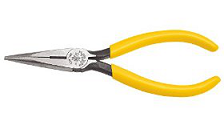
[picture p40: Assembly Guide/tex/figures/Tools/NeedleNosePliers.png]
		 &
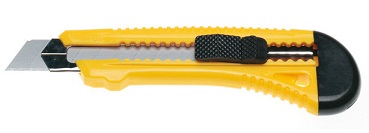
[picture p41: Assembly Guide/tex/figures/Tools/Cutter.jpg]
		 
		\\
		 Long-Nose Pliers with Side-Cutting & Cutter
		\\
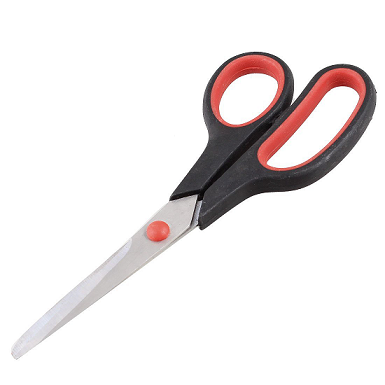
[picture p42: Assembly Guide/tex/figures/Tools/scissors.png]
		 &
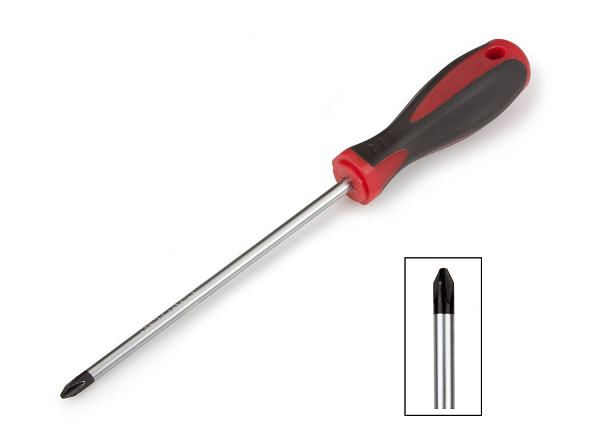
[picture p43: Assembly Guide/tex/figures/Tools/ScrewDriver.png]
		
		\\
		Scissors & Phillips Screwdriver [no. 1,2]
		\\
		 &
		
		\\
		Open-End Wrench [M3 Hex Nut] & Allen Wrench [2.5mm]		
		\\
    	\end{tabular}
}
};
\node[mytitle, right=10pt] at (box.north west) {Board 4.1: Tools};
\end{tikzpicture}%
\end{center}

\begin{center}
\begin{tikzpicture}
\node [mybox] (box){
	\scalebox{.98}{
	\begin{tabular}{ c c c }
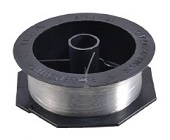
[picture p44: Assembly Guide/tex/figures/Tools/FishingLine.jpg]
		 &
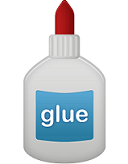
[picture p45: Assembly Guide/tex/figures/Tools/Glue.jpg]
                 &
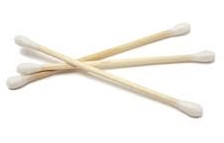
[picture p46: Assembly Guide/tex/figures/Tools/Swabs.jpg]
                \\
		Dyneema Fishing Line [0.4mm] & ABS Glue & Ear Cotton Swabs\\
		\& Nylon Fishing Line [0.4mm] & & \\
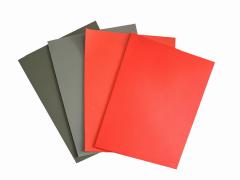
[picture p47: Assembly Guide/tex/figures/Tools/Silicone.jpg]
		 &
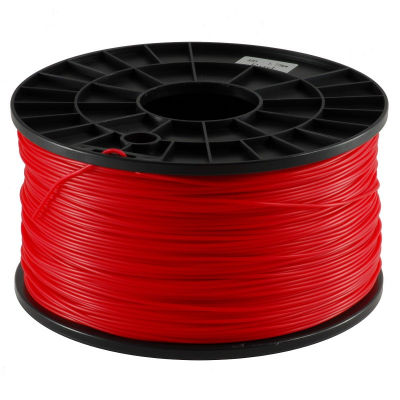
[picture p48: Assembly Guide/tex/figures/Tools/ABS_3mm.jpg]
                 & 
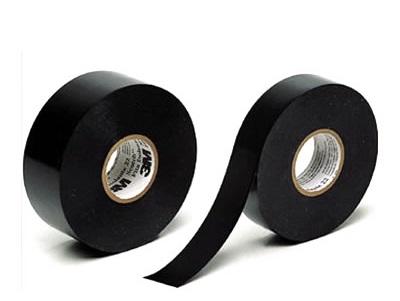
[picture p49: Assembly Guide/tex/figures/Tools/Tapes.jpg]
                
                \\
		Silicone Sheets [4mm, 5mm] & ABS filament [3mm] & Sponge, Self-Adhesive \\
		& & \& Anti-Slip Tapes \\
    	\end{tabular}
	}
};
\node[mytitle, right=10pt] at (box.north west) {Board 4.2:  Materials};
\end{tikzpicture}%
\end{center}

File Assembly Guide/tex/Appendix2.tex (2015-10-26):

\section{Parts Reference}

In this section we list all the necessary parts for the assembly of the prosthetic hand. The parts are divided in three categories: i) the finger parts, ii) the palm parts and iii) the auxiliary parts. The first category consists of all required parts to build all 5 hand fingers, the second category consists of the main palm parts, i.e., the palm structure and the whiffletree mechanism while the third category contains all required parts for building the Herkulex DRS201 servo base, the thumb mechanism, the tendon routing system and the buttons. 

In the following sections we provide a table for each category, listing all parts, along with the names of their corresponding Solidworks part files, their quantity and usage as well as an indication of whether they can be 3D printed. We also provide a separate table with all parts that can be 3D printed. Finally, to facilitate the identification of each part, we provide images of the models. 

\subsection{Finger Parts}

\begin{table}[h!]
	\centering
	\scalebox{0.87}{
		\begin{tabular}{ | l | l | l |}
			\hline
			\multicolumn{3}{|c|}{\bf{Finger Parts List}} \\
			\hline
			{\bf{Part Name}} & {\bf{Qty}} & {\bf{Description}}\\ \hline
			index & 1 & Index Finger [3D printer] \\ \hline
			middle & 1 & Middle Finger [3D printer] \\ \hline
			ring & 1 & Ring Finger [3D printer] \\ \hline
			pinky & 1 & Pinky Finger [3D printer] \\ \hline
			thumb & 1 & Thumb Finger [3D printer] \\ \hline    	
			tubePIP & 10 & Cotton Swab Tube for PIP [d:2mm, D:2.5mm, L:depending on the finger]  \\ \hline
			tubeMIP & 10 & Cotton Swab Tube for MIP [d:2mm, D:2.5mm, L:depending on the finger]  \\ \hline
			tubeDIP & 10 & Cotton Swab Tube for DIP [d:2mm, D:2.5mm, L:depending on the finger]  \\ \hline
			Joint DIP \& MIP & 5 & Silicone Sheet, 60A Durometer  [(Joint Lengthx16.2x4)mm]\\ \hline
			Joint PIP & 5 & Silicone Sheet, 60A Durometer [(Joint Lengthx16.2x5)mm]\\ \hline
			Dyneema Fishing Line & 1 & Tendon Routing [D:0.4mm, Strength:41.5kg] \\ \hline
			Deformable Spong-like Tape & 1 & [Width:10mm, Thickness:5mm] \\ \hline
			Anti-Slip Tape & 1 & 3M Gripping Material [Width:25mm] \\ \hline
			Self-Adhesive Tape & 1 & 3M Scotch 23 [Width:20mm] \\ \hline
		\end{tabular}
	}
\end{table}

\begin{center}
	\begin{tikzpicture}
	\node [mybox] (box){%
		\begin{tabular}{ c c c c}
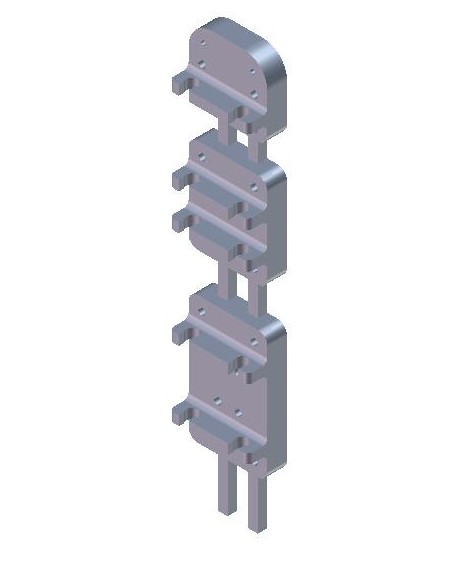
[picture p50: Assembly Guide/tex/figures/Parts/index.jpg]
		   &
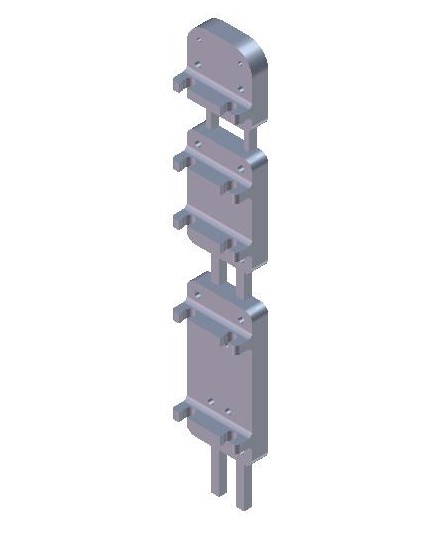
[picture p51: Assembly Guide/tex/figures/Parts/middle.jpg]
		  &
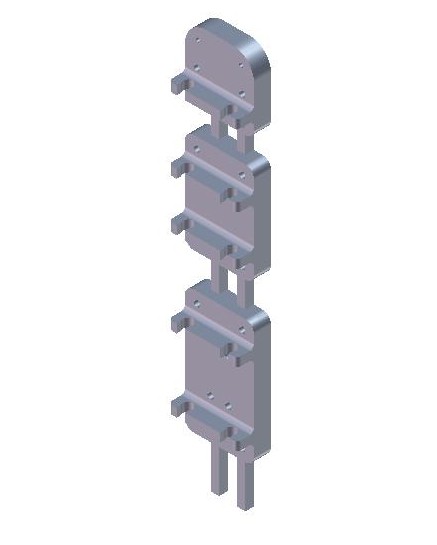
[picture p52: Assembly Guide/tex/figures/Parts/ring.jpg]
			&
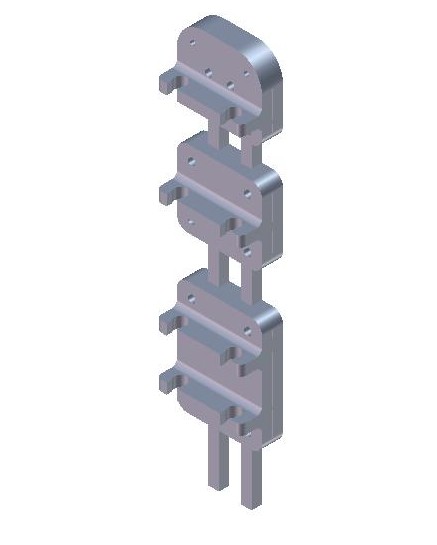
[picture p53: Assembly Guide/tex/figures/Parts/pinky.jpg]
			\\
		Index &  Middle & Ring & Pinky \\ \\
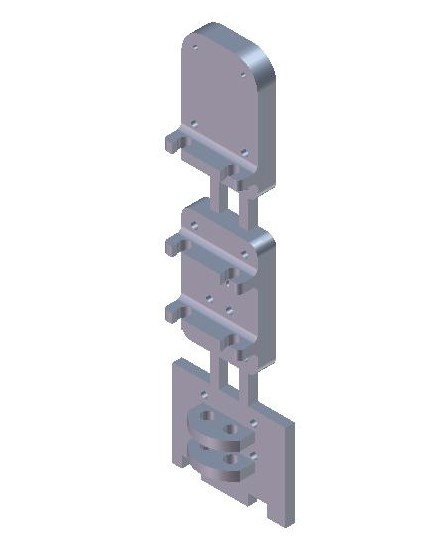
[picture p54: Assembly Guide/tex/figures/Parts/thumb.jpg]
		 &
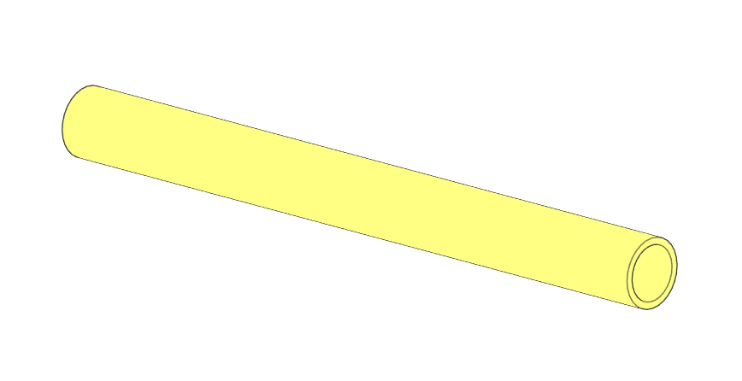
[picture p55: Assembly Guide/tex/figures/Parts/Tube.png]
		 &
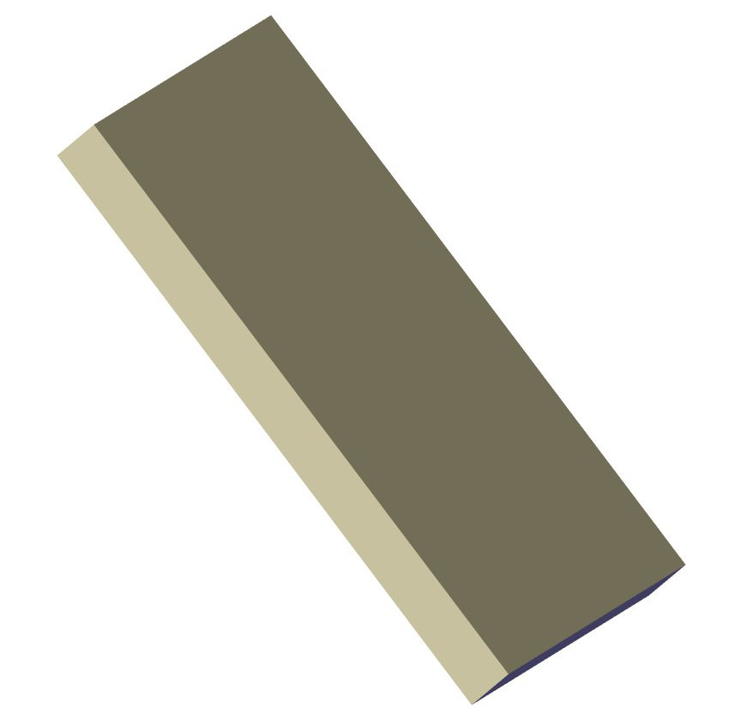
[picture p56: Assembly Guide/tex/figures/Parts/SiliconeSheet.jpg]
		 \\
		Thumb & tubes & Joint1, Joint2  \\ \\
		%		\includegraphics[width=0.9cm]{figures/Parts/WasherM3.jpg} &
		%		\includegraphics[width=1.8cm]{figures/Parts/ScrewM3x12.jpg} \\		
		%		\includegraphics[width=1cm]{figures/Parts/NutM3.jpg} &
		%		\includegraphics[width=1.4cm]{figures/Parts/Pulley.jpg} \\
		%		M3Nut & pulley  
		\end{tabular}
	};
	\node[mytitle, right=10pt] at (box.north west) {Board 5.1.1: Finger Parts};
	\end{tikzpicture}%
\end{center}

\newpage

\subsection{Palm Parts}

\begin{table}[h!]
	\centering
	\scalebox{0.84}{
		\begin{tabular}{ | l | l | l |}
			\hline
			\multicolumn{3}{|c|}{{\bf{Palm Parts List}}} \\
			\hline
			{\bf{Part Name}} & {\bf{Qty}} & {\bf{Description}}\\ \hline
			palmUp & 1 & Upside of Palm [3D printer] \\ \hline
			PalmDown & 1 & Downside of palm [3D printer] \\ \hline
			barIndexMiddle & 1 & Index \& Middle Fingers Whiphlee Tree Bar [3D printer] \\ \hline
			barRingPinky & 1 & Ring \& Pinky Fingers Whiphlee Tree Bar [3D printer] \\ \hline
			mainBar & 1 & 4 Fingers Whiphlee Tree Bar [3D printer] \\ \hline
			basePulleyInsidePalm & 4 & Tendon Routing of Thumb \& Mount of Base Flange [3D printer] \\ \hline   	    	    	    	
			Dyneema Fishing Line & 1 & Tendon Routing [D:0.4mm, Strength:41.5kg] \\ \hline
			Rubber Foam Tape & 1 & Tape for Palm [Width:10mm, Thickness:4mm] \\ \hline
			Anti-Slip Tape & 1 & 3M Gripping Material [Width:25mm] \\ \hline
			pulley & 1 & V-Groove Sealed Ball Bearing [d:3mm, D:12mm, B:4mm, Deepness:1.2mm] \\ \hline
			PlasticSpacer & 2 & Fastener [d:3.1mm, D:6mm, L:4mm] \\ \hline
			M3X12 Set Screw & 1 & Fastener, M3 Set Screw [L:12mm] \\ \hline	
			M3x16 Socket Cup Screw & 1 & Fastener, M3 Socket Cup Screw [L:16mm] \\ \hline
			M3x20 Socket Cup Screw & 2 & Fastener, M3 Socket Cup Screw [L:20mm] \\ \hline
			M3 Washer & 5 & Fastener, M3 [D:7.5, L:0.5mm] \\ \hline
			M3 Nut & 5 & Fastener, M3 Hex Nut \\ \hline
		\end{tabular}
	}
\end{table}

\vspace{0.2cm}

\begin{center}
	\begin{tikzpicture}
	\node [mybox] (box){%
		\scalebox{0.95}{
		\begin{tabular}{ c c c c }
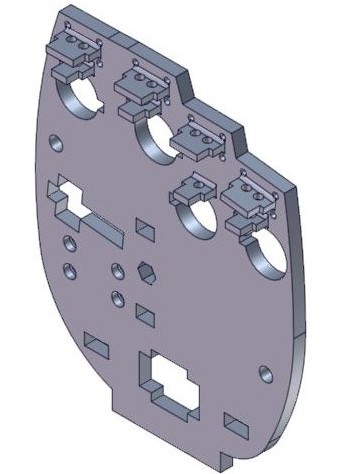
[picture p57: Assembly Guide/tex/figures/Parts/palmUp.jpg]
		 &
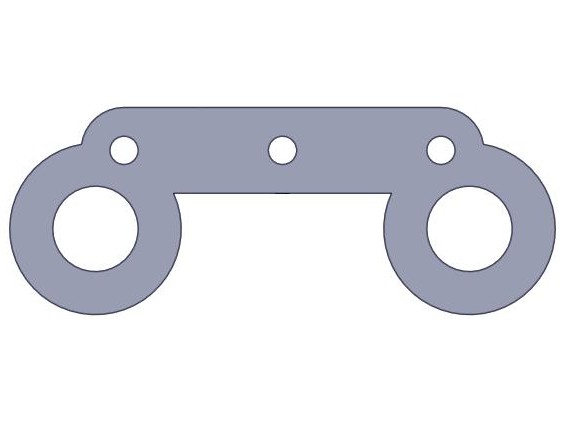
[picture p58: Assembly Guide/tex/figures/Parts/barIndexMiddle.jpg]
		 &
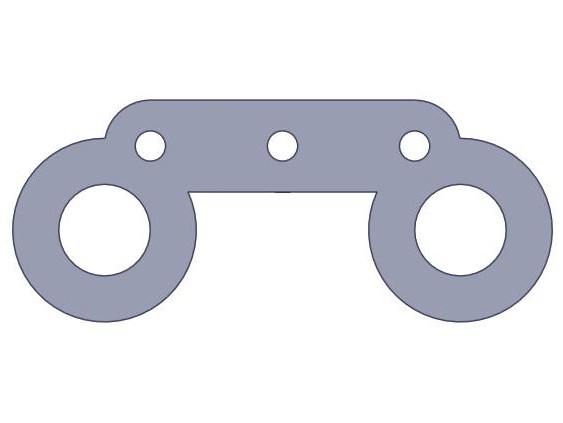
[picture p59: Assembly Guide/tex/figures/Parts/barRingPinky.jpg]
		 & 
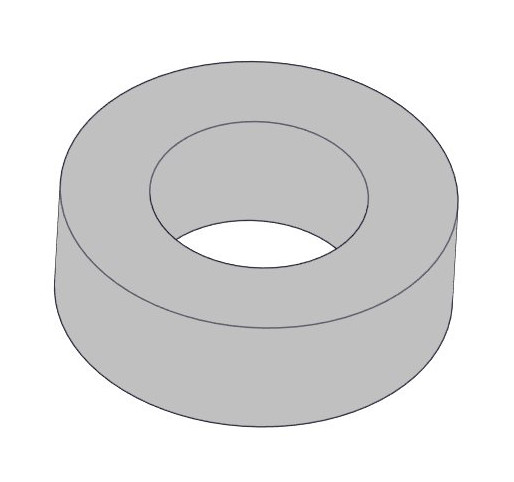
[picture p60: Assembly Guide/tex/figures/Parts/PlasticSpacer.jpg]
		 \\
		palmUp & barIndexMiddle & barRingPinky & PlasticSpacer \\
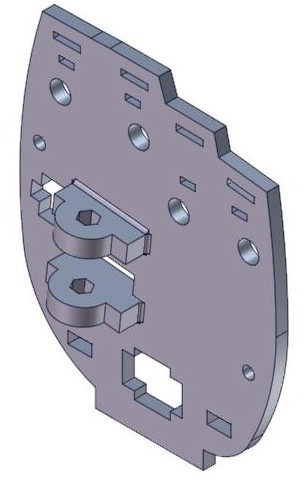
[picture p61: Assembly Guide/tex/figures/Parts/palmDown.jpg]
		 &
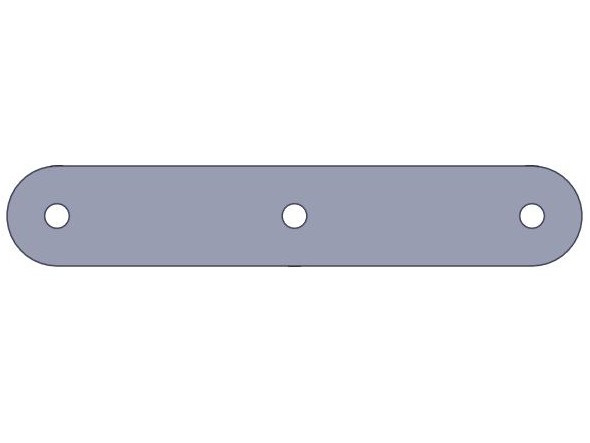
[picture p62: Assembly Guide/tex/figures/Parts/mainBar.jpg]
		 &
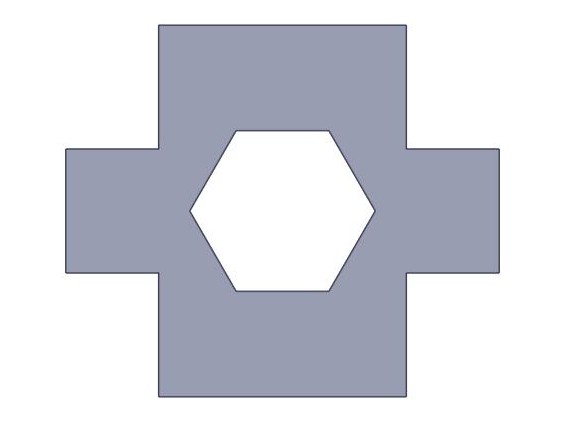
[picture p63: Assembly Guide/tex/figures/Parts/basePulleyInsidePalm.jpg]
		 &
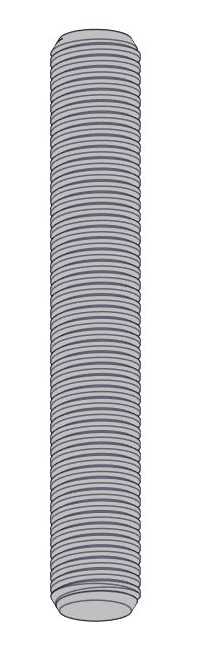
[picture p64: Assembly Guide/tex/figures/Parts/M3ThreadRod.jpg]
		 \\
		palmDown & mainBar & basePulleyInsidePalm & M3X12 Set Screw \\
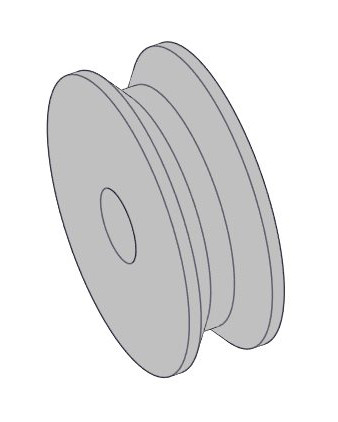
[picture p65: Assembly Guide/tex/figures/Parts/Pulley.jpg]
		 &
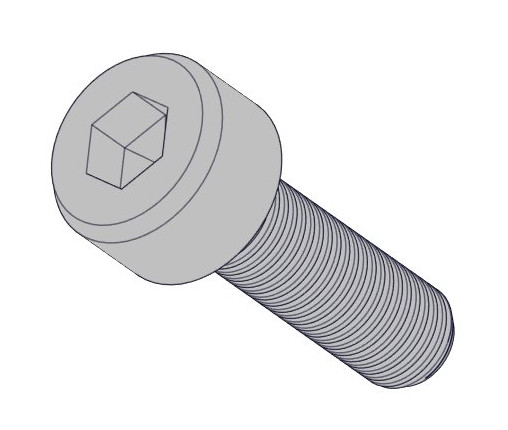
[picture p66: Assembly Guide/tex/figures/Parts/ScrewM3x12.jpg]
		 &
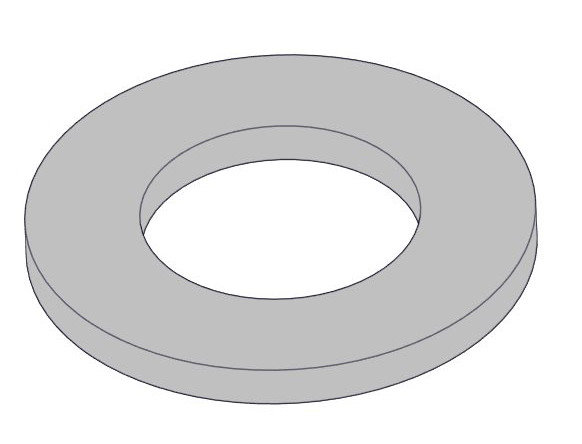
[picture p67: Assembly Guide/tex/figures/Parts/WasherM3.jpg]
		 &
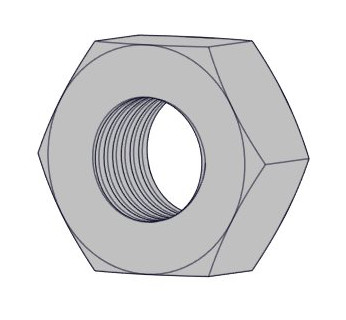
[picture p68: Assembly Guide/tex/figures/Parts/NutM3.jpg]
		 \\
		pulley & M3x16, M3x20 & M3 Washer & M3 Nut  \\
		 & Socket Cup Screw & & \\ \\
		\end{tabular}
		}
	};
	\node[mytitle, right=10pt] at (box.north west) {Board 5.2.1: Palm Parts};
	\end{tikzpicture}%
\end{center}

\newpage

\subsection{Auxiliary Parts}

\begin{table}[h!]
	\centering
	\scalebox{0.8}{
		\begin{tabular}{ | l | l | l |}
			\hline
			\multicolumn{3}{|c|}{{\bf{Auxialiary Parts List}}} \\
			\hline
			{\bf{Part Name}} & {\bf{Qty}} & {\bf{Description}}\\ \hline
			baseHerkulex & 1 & Base of HerkuleX DRS201 [3D printer] \\ \hline
			toothedMechanism & 1 & Toothed Mechanism of Base Thumb [3D printer] \\ \hline
			toothedBlockMechanism & 1 & Toothed Block Mechanism of Thumb [3D printer] \\ \hline
			thumbMovingMechanism & 1 & Thumb Moving Mechanism [3D printer] \\ \hline
			thumbButton & 1 & Thumb Base Button [3D printer] \\ \hline
			lockMechanismSupport & 1 & Support of Thumb Lock Mechanism [3D printer] \\ \hline
			lockMechanismBracket & 2 & Bracket of Thumb Lock Mechanism [3D printer] \\ \hline
			pulleyServo & 1 & Pulley of Herkulex DRS201 [3D printer] \\ \hline
			supportPulley1 & 2 & Support pulleys of tendon routing system [3D printer] \\ \hline
			supportPulleyPalmUpAssem & 1 & Support pulley of tendon routing system [3D printer] \\ \hline  	
			dovetailFemale & 1 & Dovetail Female Flange [3D printer] \\ \hline
			flangePlate & 1 & Standard Flange Plate [3D printer] \\ \hline
			buttonBase & 4 & Base of Button [3D printer] \\ \hline    	
			buttonFrame & 4 & Frame of Button [3D printer] \\ \hline 
			buttonAxle & 4 & Axle of Button [3D printer] \\ \hline     	    	    	
			Dyneema & 1 & Tendon Routing [D:0.4mm, Strength:41.5kg] \\ \hline
			HerkulexDRS-201 & 1 & Actuator\\ \hline
			pulley & 4 & V-Groove Sealed Ball Bearing [d:3mm, D:12mm, B:4mm, Deepness:1.2mm] \\ \hline
			
			PlasticSpacer & 4 & Fastener [d:3.1mm, D:6mm, L:4mm] \\ \hline
			M3X18 Set Screw & 3 & Fastener, M3 Set Screw [L:18mm]  \\ \hline	
			M3X30 Set Screw & 1 & Fastener, M3 Set Screw [L:30mm]  \\ \hline	
			M3x6 Socket Cup Screw & 1 & Fastener, M3 Socket Cup Screw [L:6mm] \\ \hline
			M3x10 Socket Cup Screw & 1 & Fastener, M3 Socket Cup Screw [L:10mm] \\ \hline
			M3 Nut & 10 & Fastener, M3 Hex Nut \\ \hline
			M3 Washer & 4 & Fastener, M3 [D:7.5mm, L:0.5mm] \\ \hline
			M2x10 Machine Screw & 4 & Fastener, M2 Machine Screw [L:10mm] \\ \hline
			M2 Nut & 4 & Fastener, M2 Hex Nut \\ \hline
			M2x16 Dowel Pin & 4 & M2 Dowel Pin [L:16mm] \\ \hline
			Compression Spring 6mm L, 9mm OD, 1mm WD & 4 & 9mm Outer Dimension, 1mm Wire Diameter [L:6mm]\\ \hline
		    Compression Spring 3mm L, 3.5mm OD, 0.5mm WD & 1 & 3.5mm Outer Dimension, 0.5mm Wire Diameter [L:3mm]  \\ \hline
		\end{tabular}
	}
\end{table}

\vspace{0.2cm}

\begin{center}
	\begin{tikzpicture}
	\node [mybox] (box){%
		\begin{tabular}{ c c c }
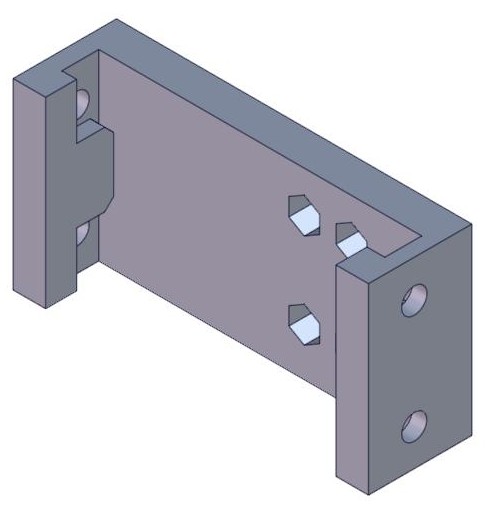
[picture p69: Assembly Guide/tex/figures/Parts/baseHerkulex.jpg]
		 &
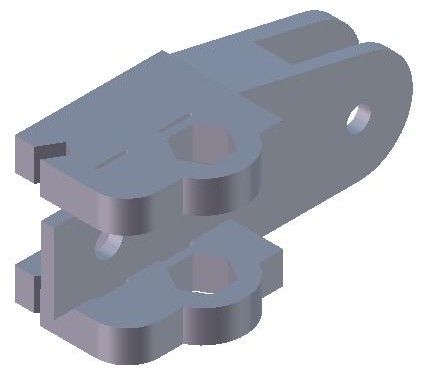
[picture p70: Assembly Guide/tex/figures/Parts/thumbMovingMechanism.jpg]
		 &
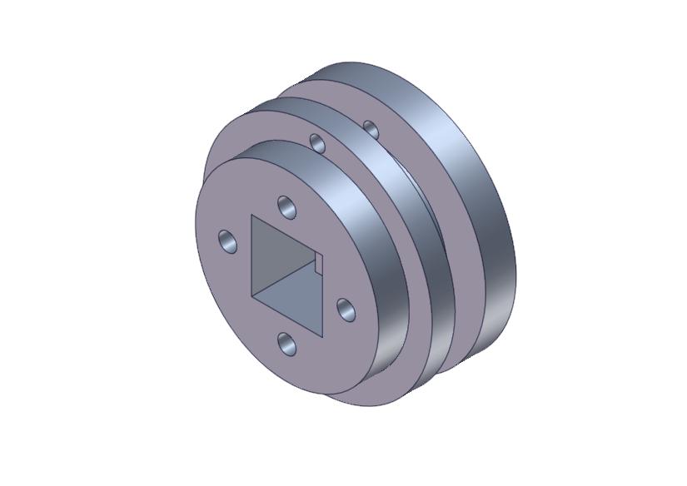
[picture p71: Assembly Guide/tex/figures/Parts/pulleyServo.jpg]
		 \\
		baseHerkulex & thumbMovingMechanism & pulleyServo \\
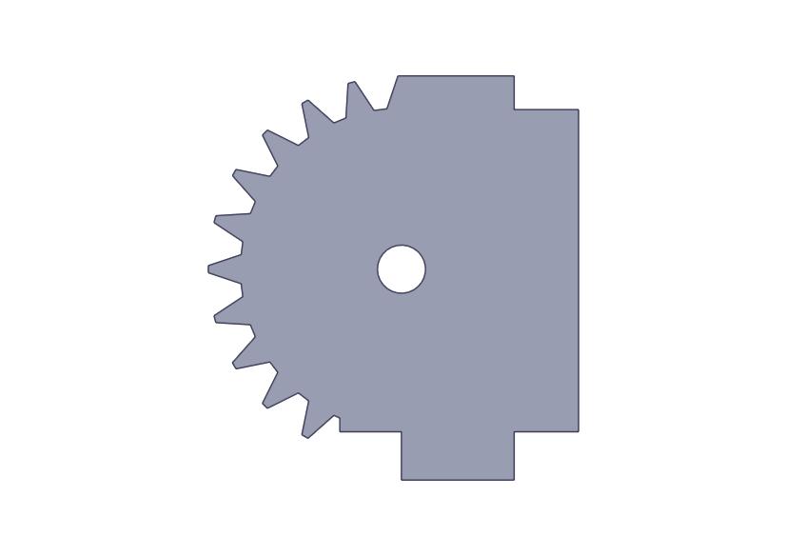
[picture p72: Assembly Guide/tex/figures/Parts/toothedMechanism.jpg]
		 &
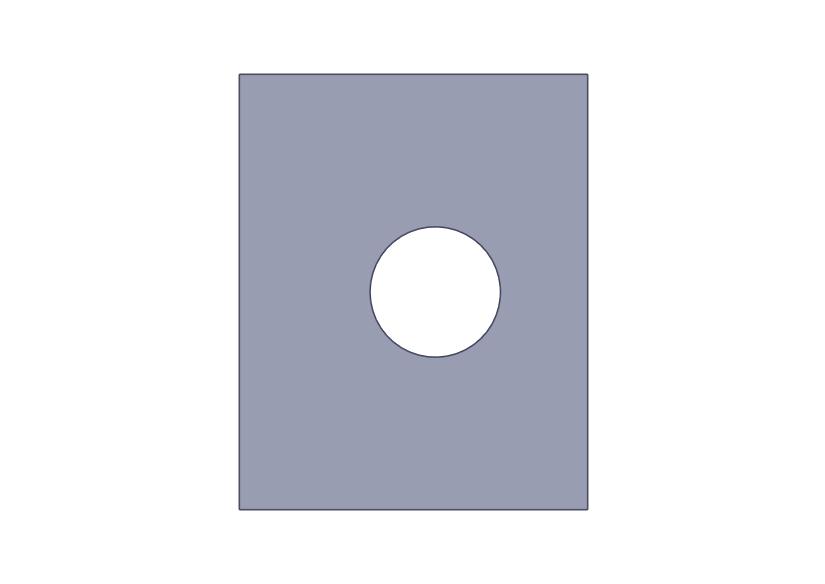
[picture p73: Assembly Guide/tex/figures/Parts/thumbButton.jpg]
		 & 
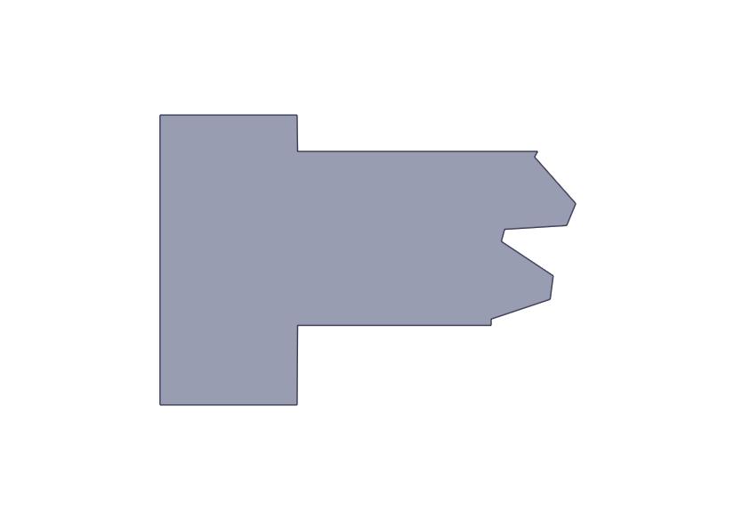
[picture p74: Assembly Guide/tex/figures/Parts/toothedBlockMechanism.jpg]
		 \\
		 toothedMechanism & thumbButton & toothedBlockMechanism  \\
		 &
		 \\
		 lockMechanismBracket &  lockMechanismSupport \\
		
		\end{tabular}
	};
	\node[mytitle, right=10pt] at (box.north west) {Board 5.3.1: Auxiliary Parts I};
	\end{tikzpicture}%
\end{center}

\newpage

\begin{center}
	\begin{tikzpicture}
	\node [mybox] (box){%
		\scalebox{0.92}{
		\begin{tabular}{ c c c }
		 &
		 & 
		 \\
		supportPulley1 & supportPulleyPalmUpAssem & dovetailFemale \\ \\
		 &
		 &
		 \\
		flangePlate & buttonBase & buttonFrame \\ \\
		 &		
		 &
		 \\
		buttonAxle & pulley & PlasticSpacer \\ \\
		 &
		 &
		 \\
		M3x6, M3x10 & M3 Nut & M3X18, M3X30 \\ 
		Socket Cup Screw & & Set Screw \\ \\
		 & 
		 &
		 \\
		M3 Washer & M2 Nut & M2x10 Machine Screw \\ \\
		\end{tabular}
		}
	};
	\node[mytitle, right=10pt] at (box.north west) {Board 5.3.2: Auxiliary Parts II};
	\end{tikzpicture}%
\end{center}

\newpage

\subsection{3D Printed Parts}

The following table contains all parts that can be 3D printed. The corresponding STL files contained in the Prosthetic-Hands/CAD directory of our GitHub reporitory (\url{www.github.com/openbionics}) are appropriate to be used with a 3D printer. 

\vspace{0.2cm}

\begin{table}[h!]
	\centering
	\scalebox{0.8}{
		\begin{tabular}{ | l | l | l | l | }
			\hline
			\multicolumn{4}{|c|}{{\bf{3D Printer Parts}}} \\
			\hline
			{\bf{Part Name}} & {\bf{Qty}} & {\bf{Description}} & {\bf{TAZ ABS Profile}}\\ \hline
			index & 1 & Index Finger & Medium, Support Off  \\ \hline
			middle & 1 & Middle Finger & Medium, Support Off \\ \hline
			ring & 1 & Ring Finger & Medium, Support Off \\ \hline
			pinky & 1 & Pinky Finger & Medium, Support Off \\ \hline
			thumb & 1 & Thumb Finger & Medium, Support Off \\ \hline 
			palmUp & 1 & Upside of Palm & Medium, Support On \\ \hline
			PalmDown & 1 & Downside of palm & Medium, Support On \\ \hline
			barIndexMiddle & 1 & Index \& Middle Fingers Whiphlee Tree Bar & Medium, Support Off \\ \hline
			barRingPinky & 1 & Ring \& Pinky Fingers Whiphlee Tree Bar & Medium, Support Off \\ \hline
			mainBar & 1 & 4 Fingers Whiphlee Tree Bar & Medium, Support Off \\ \hline
			basePulleyInsidePalm & 4  & Tendon Routing of Thumb \& Mount of Base Flange & Medium, Support Off \\ \hline
			baseHerkulex & 1 & Base of HerkuleX DRS201 & Medium, Support On \\ \hline
			toothedMechanism & 1 & Toothed Mechanism of Base Thumb & Medium, Support Off \\ \hline
			toothedBlockMechanism & 1 & Toothed Block Mechanism of Thumb & Medium, Support Off \\ \hline
			thumbMovingMechanism & 1 & Thumb Moving Mechanism & Medium, Support On \\ \hline
			thumbButton & 1 & Thumb Base Button & Medium, Support Off \\ \hline
			lockMechanismSupport & 1 & Support of Thumb Lock Mechanism & Medium, Support Off \\ \hline
			lockMechanismBracket & 2 & Bracket of Thumb Lock Mechanism & Medium, Support Off \\ \hline
			pulleyServo & 1 & Pulley of Herkulex DRS201 & Medium, Support On \\ \hline
			supportPulley1 & 2 & Support pulleys of tendon routing system & Medium, Support Off \\ \hline
			supportPulleyPalmUpAssem & 1 & Support pulley of tendon routing system & Medium, Support On \\ \hline  	
			dovetailFemale & 1 & Dovetail Female Flange & Medium, Support On \\ \hline
			flangePlate & 1 & Standard Flange Plate & Medium, Support On \\ \hline
			buttonBase & 4 & Base of Button & Medium, Support On \\ \hline    	
			buttonFrame & 4 & Frame of Button & Medium, Support On \\ \hline 
			buttonAxle & 4 & Axle of Button & Medium, Support On \\ \hline
		\end{tabular}
	}
\end{table}

\vspace{1cm}

For the replication of the prosthetic hand we use the \href{https://download.lulzbot.com/TAZ/4.0/documentation/2014Q2/manual/TAZ_4_Manual.pdf}{LulzBot TAZ 4 3D Printer} and ABS material. We used the settings of the default TAZ Slic3r profiles which can be found \href{https://www.lulzbot.com/support/taz-slic3r-profiles}{here}, except from a small set of parameters that can be found on the following table.

\vspace{1cm}

\begin{table}[h!]
	\centering
	\scalebox{1}{
		\begin{tabular}{ | l | l |}
			\hline
			\multicolumn{2}{|c|}{{\bf{3D Printer Settings}}} \\ \hline
			{\bf{Parameter}} & {\bf{Value}} \\ \hline
			Infill, Fill Density & 20\% \\ \hline
			Infill, Fill Pattern & Honeycomb \\ \hline
			Seam Position & Random \\ \hline
			Brim, Brim Width & 2 mm \\ \hline
		\end{tabular}
	}
\end{table}

\newpage

\subsection{Before Assembling}

Before starting the assembly, the following steps should be followed: \\  \\
$\bullet$ Smoothen the acrylic parts with sandpaper. \\ \\
$\bullet$ Treat the ABS parts with acetone (e.g. see \href{http://blog.reprap.org/2013/02/vapor-treating-abs-rp-parts.html}{reprap Blog}).\\ \\
$\bullet$ Cut the cotton swabs to the appropriate size (following the parts reference dimensions). \\ \\
$\bullet$ Cut the silicone sheets to the appropriate size (following the parts reference dimensions). \\ \\
$\bullet$ Group the parts according to the parts reference. \\ \\
$\bullet$ Pay increased attention to the steps followed by the following icon: \circled{!}\\ \\
%$\bullet$ Note that the provided models do not have the actual size of the parts.\\ \\

\begin{center}
	\begin{tikzpicture}
	\node [mybox] (box){%
		\begin{tabular}{ c }
		 \\
		Cutting the silicone sheets with a cutter and a ruler.
		\end{tabular}
	};
	\node[mytitle, right=10pt] at (box.north west) {Board 5.5.1: Silicone Sheets Preparation};
	\end{tikzpicture}%

\end{center}

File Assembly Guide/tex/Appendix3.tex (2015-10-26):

\section{Fingers Assembly}

This section contains instructions for assembling all 5 fingers of the prosthetic hand. Before each assembly step, a table containing all required materials and tools will be provided for convenience.

\subsection{Assembling the Phalanges}

%The parts and the materials you will need to assemble the fingers are listed in table \ref{phalangespartsmaterials}. The phalanges for all fingers of the hand can be assembled by gluing the parts of the following table, following the illustrated instructions of the the figures below. 

\begin{table}[ht!]
	\centering
	%\begin{minipage}[b]{0.50\linewidth}\centering
		\scalebox{1}{
			\begin{tabular}{ | c | c |}
				\hline
				\multicolumn{2}{|c|}{\bf{Part List 6.1.1}} \\
				\hline
				{\bf{Part Name}} & {\bf{Qty}}\\ \hline
				index & 1  \\ \hline
				middle & 1  \\ \hline
				ring & 1  \\ \hline
				pinky & 1  \\ \hline
				thumb & 1 \\ \hline
				tubeMIP & 8  \\ \hline
				tubePIP & 10  \\ \hline
				tubeDIP & 10  \\ \hline
				%		M3Washer & 16 \\ \hline
				%		M3Nut & 4 \\ \hline
				%		pulley & 4 \\ \hline
				\multicolumn{2}{|c|}{\textbf{Materials}} \\
				\hline
				\multicolumn{2}{|c|}{Super Glue } \\				
				\hline
			\end{tabular}				
		}
	%\end{minipage}
	
	%\caption{Parts and materials needed to assemble the phalanges.}
	%\label{phalangespartsmaterials}
\end{table}

%\begin{table}[ht!]
%	\centering
%	%\begin{minipage}[b]{0.50\linewidth}\centering
%
%	%\end{minipage}
%\end{table}

\begin{figure}[h]
	\centering
	\begin{tikzpicture}
	\node [mybox] (box){%
		\begin{minipage}[b]{0.45\textwidth}%\centering
		\begin{tabular}{ l l}
		{\circled{1}} & {Insert the low friction tubes to}\\
		{} & {the tubePIP/tubeMIP plates.} \\ \\
		{\circled{2}} & {Glue the edges of the tubes to}\\
		{} &  {the tube plates with super glue.}\\
		\end{tabular}
		\end{minipage}
		%\hspace{0.5cm}	
		\begin{minipage}[b]{0.4\textwidth}
		\begin{tabular}{ l }
		
		\end{tabular}
		\end{minipage}
	};
	%\node[anchor=south] at (-5,3.7) {\textbf{PIP and MIP Phalanges}}; % or (current bounding box.north) {Some Text};
	\node[mytitle, right=10pt] at (box.north west) {Board 6.1.1: Assembling PIP/MIP Phalanges};
	\end{tikzpicture}%
\end{figure}

\begin{figure}[!htbp]
	\centering
	\begin{tikzpicture}
	\node [mybox] (box){%
		\begin{minipage}[b]{0.45\linewidth}
		\begin{tabular}{l l}
		{\circled{1}} & {Insert the low friction tubes to the}\\
		{} & {tubeDIP plate.} \\ \\
		{\circled{2}} & {Glue the edges of the tubes to the}\\
		{} &  {tubeDIP plate with super glue.}\\
		\end{tabular}
		\end{minipage}
		%\hspace{0.5cm}	
		\begin{minipage}[b]{0.45\linewidth}
		\begin{tabular}{ l }
		
		\end{tabular}
		\end{minipage}
	};
	\node[mytitle, right=10pt] at (box.north west) {Board 6.1.2: Assembling DIP Phalange};
	\end{tikzpicture}%
\end{figure}

\begin{figure}[h]
	\centering
	\begin{tikzpicture}
	\node [mybox] (box){%
		\begin{minipage}[b]{.3\textwidth}
		\begin{tabular}{ c }
		
		\end{tabular}
		\end{minipage}	
		\begin{minipage}[b]{0.3\textwidth}
		\begin{tabular}{ c }
		
		\end{tabular}
		\end{minipage}
		\begin{minipage}[b]{0.3\textwidth}
		\begin{tabular}{ c }
		
		\end{tabular}
		\end{minipage}
	};
	\node[anchor=south] at (5.5,-1.2) {\textbf{DIP}};
	\node[anchor=south] at (0.5,-1.2) {\textbf{MIP}};
	\node[anchor=south] at (-4,-1.2) {\textbf{PIP}};	
	\node[mytitle, right=10pt] at (box.north west) {Board 6.1.3: Completed Phalanges};
	\end{tikzpicture}%
\end{figure}

\newpage

\subsection{Attaching the Phalanges on the Flexure Joints }

The flexure joints of each finger are implemented with silicone sheets, attached to each pair of neighboring phalanges via simple stitching with nylon fishing line and long needles as shown in the following assembly steps. 

\begin{table}[ht!]
	\centering
		\centering
		\scalebox{1}{
			\begin{tabular}{ | c | c |}
				\hline
				\multicolumn{2}{|c|}{{\textbf{Part List 6.2.1}}} \\\hline								
				{\bf{Par Namet}} & {\bf{Qty}}\\ \hline
				index & 1  \\ \hline
				middle & 1  \\ \hline
				ring & 1  \\ \hline
				pinky & 1  \\ \hline
				thumb & 1 \\ \hline
				Joint DIP \& MIP & 4  \\ \hline
				Joint PIP & 5  \\ \hline
				\multicolumn{2}{|c|}{{\textbf{Tools}}} \\\hline				
				\multicolumn{2}{|c|}{{{Long Needles}}} \\\hline
				\multicolumn{2}{|c|}{{Nylon Fishing Line}} \\\hline
				\multicolumn{2}{|c|}{{{Cutter}}} \\\hline
				\multicolumn{2}{|c|}{{{Long-Nose Pliers with Side-Cutting}}} \\\hline
				\multicolumn{2}{|c|}{{{Precision Ruler}}} \\\hline
				\multicolumn{2}{|c|}{{{Scissors}}} \\\hline
			\end{tabular}
		}
	%\caption{Parts and tools needed to attach the phalanges to the flexure joints.}
	%\label{attachingparts}		
\end{table}

%	\begin{minipage}[b]{0.45\linewidth}
%		\centering
%		\scalebox{1}{
%			\begin{tabular}{ | c |}
%				\hline
%				\multicolumn{1}{|c|}{{\bf{Tools}}} \\
%				\hline
%				Long Needles \\ \hline
%				Nylon Fishing Line \\ \hline
%				Cutter \\ \hline
%				Long-Nose Pliers with Side-Cutting \\ \hline
%				Precision Ruler \\ \hline
%				Scissors \\ \hline
%			\end{tabular}
%		}
%	\end{minipage}	

Board 6.2.1 displayes an overview of the stitching patterns. The red lines denote stitching that passes from both sides of the rigid part and the flexure joint, while the blue lines depict a fishing line that passes only from the lower side of the flexure joint. 

\begin{figure}[h]
	\centering
	\begin{tikzpicture}
	\node [mybox] (box){%
		\begin{minipage}[b]{0.45\textwidth}
		\centering
		\begin{tabular}{ l }
		
		\end{tabular}
		\end{minipage}
		\begin{minipage}[b]{0.45\textwidth}
		\centering
		\begin{tabular}{ r }
		
		\end{tabular}
		\end{minipage}
	};	
	\node[mytitle, right=10pt] at (box.north west) {Board 6.2.1: Phalange/Joint Attachment Overview};
	\end{tikzpicture}%
\end{figure}

\newpage

The stitching steps are illustrated in the following figures.

\begin{center}
	\begin{tikzpicture}
	\node [mybox] (box){%
		\begin{minipage}[b]{0.45\linewidth}
		\begin{tabular}{ l }
		 
		\end{tabular}
		\end{minipage}
		\begin{minipage}[b]{0.45\linewidth}
		\begin{tabular}{ l l}
		{\circled{1}} &  {Cut 450mm of fishing line.}\\ \\
		{\circled{2}} & {Pass the fishing line through}\\
		{} &  {the eyes of the needles.}\\ \\
		{\circled{3}} & {Insert the needles into the upper,}\\
		{} & { and outer slots of PIP.}\\
		\end{tabular}
		\end{minipage}
	};
	\node[mytitle, right=10pt] at (box.north west) {Board 6.2.2: Stitching Step I};
	\end{tikzpicture}%
\end{center}

\begin{center}
	\begin{tikzpicture}
	\node [mybox] (box){%
		\begin{minipage}[b]{0.45\linewidth}
		\begin{tabular}{ l l }
		{\circled{1}} & {Pass each needle through the eye}\\
		{} &  {of the other.}\\ \\
		{\circled{2}} & {Repeat step \circled{1} twice.}\\ \\
		{\circled{!}} & {The needles are now in the lower}\\
		{} & {side of MIP.}\\ \\
		{\circled{3}} & {Insert the needles into the inner slots}\\ 
		{} &  {of MIP.} \\
		\end{tabular}
		\end{minipage}
		\begin{minipage}[b]{0.45\linewidth}
		\begin{tabular}{ l }
		
		\end{tabular}
		\end{minipage}
	};
	\node[mytitle, right=10pt] at (box.north west) {Board 6.2.3: Stitching Step II};
	\end{tikzpicture}%
\end{center}

\begin{center}
	\begin{tikzpicture}
	\node [mybox] (box){%
		\begin{minipage}[b]{0.45\linewidth}
		\begin{tabular}{ l }
		 
		\end{tabular}
		\end{minipage}
		\begin{minipage}[b]{0.45\linewidth}
		\begin{tabular}{ l l }
		{\circled{1}} & {Pass each needle from the eye of the}\\
		{} &  {other.} \\ \\
		{\circled{2}} & {Repeat step \circled{1} 3 times.}\\ \\
		{\circled{!}} & {The needles are now in the lower side}\\
		{} & {of MIP.}\\
		\end{tabular}
		\end{minipage}
	};
	\node[mytitle, right=10pt] at (box.north west) {6.2.4: Stitching Step III};
	\end{tikzpicture}%
\end{center}

\begin{center}
	\begin{tikzpicture}
	\node [mybox] (box){%
		\begin{minipage}[b]{0.55\linewidth}
		\begin{tabular}{ l l}
		{\circled{1}} & {Remove the needles from the}\\
		{} & {fishing line.} \\ \\
		{\circled{2}} & {Tie the ends of the fishing line}\\
		{} & {with multiple surgeon's knots.}\\
		\end{tabular}
		\end{minipage}
		\begin{minipage}[b]{0.35\linewidth}
		\begin{tabular}{ r }
		
		\end{tabular}
		\end{minipage}
	};
	\node[mytitle, right=10pt] at (box.north west) {Board 6.2.5: Stitching Step IV};
	\end{tikzpicture}%
\end{center}

\begin{center}
	\begin{tikzpicture}
	\node [mybox] (box){%
		\begin{minipage}[b]{0.45\linewidth}
		\begin{tabular}{ l l}
		{\circled{1}} & {Cut 450mm of fishing line.} \\ \\
		{\circled{2}} & {Pass the fishing line through}\\
		{} &  {the slots of two long needles.} \\ \\
		%		\circled{3} Center the fingerPIP part with the silicone part\\ and align it with the line from the previous step.\\
		{\circled{3}} &  {Insert the needles in the lower,}\\
		{} &  {outer holes of PIP.} \\
		\end{tabular}
		\end{minipage}
		\begin{minipage}[b]{0.45\linewidth}
		\begin{tabular}{ c }
		 
		\end{tabular}
		\end{minipage}
	};
	\node[mytitle, right=10pt] at (box.north west) {Board 6.2.6: Stitching Step V};
	\end{tikzpicture}%
\end{center}

\begin{center}
	\begin{tikzpicture}
	\node [mybox] (box){%
		\begin{minipage}[b]{0.45\linewidth}\centering
		\begin{tabular}{ l }
		
		\end{tabular}
		\end{minipage}
		\hspace{0.5cm}	
		\begin{minipage}[b]{0.45\linewidth}
		\begin{tabular}{ l l}
		{\circled{1}} & {Pass each needle through the eye}\\
		{} & {of each other.} \\ \\
		{\circled{2}} & {Repeat step \circled{1} 3 times.} \\ \\
		{\circled{!}} &  {The needles are now in the lower}\\
		{} & {side of PIP.}\\
		\end{tabular}
		\end{minipage}
	};
	\node[mytitle, right=10pt] at (box.north west) {Board 6.2.7: Stitching Step VI};
	\end{tikzpicture}%
\end{center}

\begin{center}
	\begin{tikzpicture}
	\node [mybox] (box){%
		\begin{minipage}[b]{0.45\linewidth}\centering
		\begin{tabular}{ l l }
		{\circled{1}} & {Insert the needles into the inner,}\\
		{} & {lower slots of PIP.}\\ \\
		{\circled{2}} & {Pass each needle through the eye}\\
		{} & {of each other.}\\ \\
		{\circled{3}} & {Repeat step \circled{2} 3 times.}\\ \\
		{\circled{!}} & {The needles are now in the lower}\\
		{} &  {side of PIP.} \\ \\
		{\circled{4}} & {Remove the needles from the}\\
		{} &  {fishing line.}\\ \\
		{\circled{5}} & {Tie the ends of the fishing line}\\
		{} &  {with multiple surgeon's knots.}\\
		\end{tabular}
		\end{minipage}
		\hspace{0.5cm}	
		\begin{minipage}[b]{0.45\linewidth}
		\begin{tabular}{ c }
		
		\end{tabular}
		\end{minipage}
	};
	\node[mytitle, right=10pt] at (box.north west) {Board 6.2.8: Stitching Step VII};
	\end{tikzpicture}%
\end{center}

\begin{center}
	\begin{tikzpicture}
	\node [mybox] (box){%
		\begin{minipage}[b]{0.45\linewidth}\centering
		\begin{tabular}{ l }
		
		\end{tabular}
		\end{minipage}
		\hspace{0.5cm}	
		\begin{minipage}[b]{0.45\linewidth}
		\begin{tabular}{ l l}
		{\circled{1}} & {Repeat steps 6.2.5 - 6.2.7 for DIP.} \\ \\
		{\circled{!}} & {Congratulations, you built a finger!}
		\end{tabular}
		\end{minipage}
	};
	\node[mytitle, right=10pt] at (box.north west) {Board 6.2.9: Completed Finger};
	\end{tikzpicture}%
\end{center}

\newpage

\subsection{Tendon Routing System Assembly}

\begin{table}[h]
	\centering
	%\begin{minipage}[b]{0.50\linewidth}\centering
		\scalebox{0.97}{
			\begin{tabular}{ | c | c |}
				\hline
				\multicolumn{2}{|c|}{{\textbf{Part List 6.3.1}}} \\ \hline	
				{\bf{Part Name}} & {\bf{Qty}}\\ \hline
				index & 1  \\ \hline
				middle & 1  \\ \hline
				ring & 1  \\ \hline
				pinky & 1  \\ \hline
				thumb & 1 \\ \hline
				\multicolumn{2}{|c|}{{\bf{Tools \& Materials}}} \\ \hline
				\multicolumn{2}{|c|}{{Scissors}} \\ \hline
				\multicolumn{2}{|c|}{{Dyneema}} \\ \hline
				
				%		Precision Ruler \\ \hline
				
			\end{tabular}
		}	
\end{table}

\vspace{0.2cm}

\begin{center}
	\begin{tikzpicture}
	\node [mybox] (box){%
		\begin{minipage}[b]{0.45\linewidth}\centering
		\begin{tabular}{ c }
		
		\end{tabular}
		\end{minipage}
		\hspace{0.5cm}	
		\begin{minipage}[b]{0.50\linewidth}
		\begin{tabular}{ l l}
		{\circled{1}} & {Cut 600mm of fishing line.} \\ \\
		{\circled{2}} & {Pass the Dyneema through the phalange}\\
		{} & {tubes starting from PIP.} \\
		\end{tabular}
		\end{minipage}
	};
	\node[mytitle, right=10pt] at (box.north west) {Board 6.3.1: Passing the Dynema from the Phalange Tubes};
	\end{tikzpicture}%
\end{center}

\vspace{0.2cm}

\begin{center}
	\begin{tikzpicture}
	\node [mybox] (box){%
		\begin{minipage}[b]{0.45\linewidth}\centering
		\begin{tabular}{ c }
		
		\end{tabular}
		\end{minipage}
		\hspace{0.5cm}	
		\begin{minipage}[b]{0.50\linewidth}
		\begin{tabular}{ l l }
		{\circled{1}} & {Tie the ends of Dyneema with}\\
		{} & {multiple \href{https://en.wikipedia.org/wiki/Surgeon%27s_knot}{surgeon's knots}.} \\
		\end{tabular}
		\end{minipage}
	};
	\node[mytitle, right=10pt] at (box.north west) {Board 6.3.2: Fixing the Dynema on the Fingers};
	\end{tikzpicture}%
\end{center}

\newpage

\subsection{Attaching the Soft Fingetips on the Fingers}

\begin{table}[ht!]
		\centering
		\scalebox{0.97}{
			\begin{tabular}{ | c | c |}
				\hline
				\multicolumn{2}{|c|}{{\textbf{Parts List 6.4.1}}} \\\hline	
				{\bf{Part Name}} & {\bf{Qty}}\\ \hline
				index & 1  \\ \hline
				middle & 1  \\ \hline
				ring & 1  \\ \hline
				pinky & 1  \\ \hline
				thumb & 1 \\ \hline
				\multicolumn{2}{|c|}{{\bf{Tools \& Materials}}} \\\hline
				\multicolumn{2}{|c|}{{Scissors}} \\ \hline
				\multicolumn{2}{|c|}{{Self-Adhesive Tape}} \\ \hline
				\multicolumn{2}{|c|}{{Deformable Spong-like Tape}} \\ \hline
				\multicolumn{2}{|c|}{{Anti-Slip Tape}} \\ \hline			
			\end{tabular}
		}	
\end{table}

\vspace{0.2cm}

\begin{center}
	\begin{tikzpicture}
	\node [mybox] (box){%
		\begin{minipage}[b]{0.45\linewidth}\centering
		\begin{tabular}{ c }
		
		\end{tabular}
		\end{minipage}
		\hspace{0.5cm}	
		\begin{minipage}[b]{0.45\linewidth}
		\begin{tabular}{ l l }
		{\circled{1}} & {Cut two pieces of sponge-like tape}\\
		{} & {to the size of PIP.} \\ \\
		{\circled{2}} & {Attach the tape pieces on PIP.} \\
		\end{tabular}
		\end{minipage}
	};
	\node[mytitle, right=10pt] at (box.north west) {Board 6.4.1: PIP Inner Coating};
	\end{tikzpicture}%
\end{center}

\vspace{0.2cm}

\begin{center}
	\begin{tikzpicture}
	\node [mybox] (box){%
		\begin{minipage}[b]{0.45\linewidth}\centering
		\begin{tabular}{ l l}
		{\circled{1}} & {Cut 130mm of self-adhesive tape.} \\ \\
		{\circled{2}} & {Wrap the tape around PIP.} \\
		\end{tabular}
		\end{minipage}
		\hspace{0.5cm}	
		\begin{minipage}[b]{0.45\linewidth}
		\begin{tabular}{ c }
		
		\end{tabular}
		\end{minipage}
	};
	\node[mytitle, right=10pt] at (box.north west) {Board 6.4.2: Fixing PIP Coating};
	\end{tikzpicture}%
\end{center}

\vspace{0.2cm}

\begin{center}
	\begin{tikzpicture}
	\node [mybox] (box){%
		\begin{minipage}[b]{0.45\linewidth}\centering
		\begin{tabular}{ c }
		
		\end{tabular}
		\end{minipage}
		\hspace{0.5cm}	
		\begin{minipage}[b]{0.45\linewidth}
		\begin{tabular}{ l l}
		{\circled{1}} & {Cut two pieces of sponge-like tape}\\
		{} &  {to the size of DIP.} \\ \\
		{\circled{2}} & {Attach the pieces on DIP.} \\
		%		\circled{3} Cut a piece of 10mm sponge tape. \\
		%		\circled{4} Set the sponge tape onto the empty space \\ of the Finger DIP. \\
		%		\circled{5} Cut two pieces of 40mm sponge tape and \\ set them onto the other side.
		\end{tabular}
		\end{minipage}
	};
	\node[mytitle, right=10pt] at (box.north west) {Board 6.4.3: DIP Inner Coating};
	\end{tikzpicture}%
\end{center}

\vspace{0.2cm}

\begin{center}
	\begin{tikzpicture}
	\node [mybox] (box){%
		\begin{minipage}[b]{0.45\linewidth}\centering
		\begin{tabular}{ c }
		
		\end{tabular}
		\end{minipage}
		\hspace{0.5cm}	
		\begin{minipage}[b]{0.45\linewidth}
		\begin{tabular}{ l l }
		{\circled{1}} & {Cut 200mm of self-adhesive tape.} \\ \\
		{\circled{2}} & {Wrap the tape around the DIP.} \\
		\end{tabular}
		\end{minipage}
	};
	\node[mytitle, right=10pt] at (box.north west) {Board 6.4.4: Fixing DIP Coating};
	\end{tikzpicture}%
\end{center}

\newpage

\begin{center}
	\begin{tikzpicture}
	\node [mybox] (box){%
		\begin{minipage}[b]{0.4\linewidth}\centering
		\begin{tabular}{ l l }
		{\circled{1}} & {Cut a piece of anti-slip tape}\\
		{} & {to the size of PIP.} \\ \\
		{\circled{2}} & {Attach the tape on PIP.} \\ \\
		{\circled{3}} & {Cut a piece of anti-slip tape}\\
		{} & {to the size of DIP.} \\ \\
		{\circled{4}} & {Attach the tape on DIP.} \\ \\
		{\circled{!}} & {Cut the edges of the tape.} \\ \\
		\end{tabular}
		\end{minipage}
		\begin{minipage}[b]{0.53\linewidth}
		\begin{tabular}{ c }
		
		\end{tabular}
		\end{minipage}
	};
	\node[mytitle, right=10pt] at (box.north west) {Board 6.4.5: Anti-Slip Coating};
	\end{tikzpicture}%
\end{center}

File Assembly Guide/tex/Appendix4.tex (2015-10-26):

\section{Hand Assembly}

This section contains illustrated instructions for assembling all remaining hand components and for attaching them on the palm. For each assembly step, a table listing all necessary parts and tools/materials will be provided for convenience.

\subsection{Attaching the Fingers on the Palm}

%The necessary parts and tools to attach all fingers on the palm are listed in table \ref{fingerspalmattachment}, while Fig. 7.1.1 demonstrates the assembly.

\begin{table}[ht!]
	\centering
	\begin{tabular}{ | c | c | c |}
		\hline
		\multicolumn{3}{|c|}{{\textbf{Parts List 7.1.1}}} \\ \hline		
		{\bf{No}} & {\bf{Part Name}} & {\bf{Qty}}\\ \hline
    		1 & index & 1  \\ \hline
    		2 & middle & 1  \\ \hline
		3 & ring & 1 \\ \hline
		4 & pinky & 1 \\ \hline
		5 & palmUp & 1 \\ \hline
		\multicolumn{3}{|c|}{{\textbf{Tools}}} \\ \hline
		\multicolumn{3}{|c|}{{{Long Needles}}} \\ \hline
		\multicolumn{3}{|c|}{{{Nylon Fishing Line}}} \\ \hline
		\multicolumn{3}{|c|}{{{Cutter}}} \\ \hline
		\multicolumn{3}{|c|}{{{Long-Nose Pliers with Side-Cutting}}} \\ \hline
		\multicolumn{3}{|c|}{{{Scissors}}} \\ \hline
		
    	\end{tabular}
\end{table}

\vspace{0.5cm}

\begin{center}
\begin{tikzpicture}
\node [mybox] (box){%

  	\begin{minipage}[b]{0.45\linewidth}\centering
	\begin{tabular}{ c }
		
    	\end{tabular}
	\end{minipage}
	
	\hspace{1.0cm}	
	
	\begin{minipage}[b]{0.4\linewidth}\centering
	\begin{tabular}{  l  l }
		{\circled{1}} & {Stitch fingers parts 1-4}\\
		{} & {on the palm following}\\
		{} &  {the procedure described}\\
		{} & {in steps 6.2.5 - 6.2.7.}\\
	\end{tabular}
  	\end{minipage}
	};
\node[mytitle, right=10pt] at (box.north west) {Board 7.1.1: Attaching the Fingers on the Palm};
\end{tikzpicture}%
\end{center}

\newpage

\subsection{Building/Attaching the Locking Buttons on the Palm}

\begin{table}[ht!]
	\centering
  	%\begin{minipage}[b]{0.50\linewidth}\centering
	\scalebox{0.97}{
	\begin{tabular}{ | c | c | c |}
		\hline
		\multicolumn{3}{|c|}{{\textbf{Parts List 7.2.1}}} \\ \hline
		{\bf{No}} & {\bf{Part Name}} & {\bf{Qty}}\\ \hline
     	1 & palmUp & 1  \\ \hline
		2 & buttonBase & 4 \\ \hline
		\multicolumn{3}{|c|}{{\bf{Material}}} \\ \hline
		\multicolumn{3}{|c|}{{{ABS Glue}}} \\ \hline
	\end{tabular}
	}
	%\caption{The Parts required to build the button bases on the Palm along with the glue type.}
	%\label{buttonspalm}
\end{table}

\begin{center}
\begin{tikzpicture}
\node [mybox] (box){%
  	\begin{minipage}[b]{0.50\linewidth}\centering
	\begin{tabular}{ l }
           	      
    	\end{tabular}
	\end{minipage}
	\begin{minipage}[b]{0.4\linewidth}
	\begin{tabular}{  l  l }
		{\circled{1}} & {Glue the buttonBase parts}\\
		{} & {on the palmUp part in the}\\
		{} & {designated positions.}\\
    	\end{tabular}
  	\end{minipage}
};
\node[mytitle, right=10pt] at (box.north west) {Board 7.2.1: Attaching the Button Bases on the Palm};
\end{tikzpicture}%
\end{center}

\begin{table}[ht!]
\centering
	\scalebox{0.97}{
	\begin{tabular}{ | c | c | c |}
		\hline
		\multicolumn{3}{|c|}{{\bf{Parts List 7.2.2}}}\\ \hline
		{\bf{No}} & {\bf{Part Name}} & {\bf{Qty}}\\ \hline
    		1 & buttonAxle & 4  \\ \hline
   		2 & buttonFrame & 4  \\ \hline
        3 & M2X16 Dowel Pin & 4 \\ \hline
		4 & Compression Spring 6mm L, & 4 \\  & 9mm OD, 1mm WD  & \\ \hline
		5 & Structure of Board 7.2.1 & 1 \\ \hline
 		\multicolumn{3}{|c|}{{\bf{Tools/Materials}}} \\ \hline
 		\multicolumn{3}{|c|}{{{ABS Glue}}} \\ \hline
 		\multicolumn{3}{|c|}{{{Long-Nose Pilers with Side-Cutting}}} \\ \hline		
    	\end{tabular}
	}
\end{table}

\begin{center}
\begin{tikzpicture}
\node [mybox] (box){%
	\begin{minipage}[b]{0.50\linewidth}
	\begin{tabular}{ l }
 	 	 
    	\end{tabular}
  	\end{minipage}
  	\begin{minipage}[b]{0.50\linewidth}\centering
	\begin{tabular}{ l l}
		{\circled{1}} & {Glue the buttonFrame parts}\\
		{} & {on the buttonBase's (see Parts List/}\\
		{} & {Board 7.2.1).} \\ \\
		{\circled{2}} & {Insert the compression springs in}\\
		{} & {the buttonFrame slots.} \\ \\
		{\circled{3}} & {Insert the buttonAxle parts in the}\\
		{} & {buttonFrame slots.} \\ \\
		{\circled{4}} & {Insert the M2X16 pins in the}\\
		{} & {buttonAxle slots.} \\            
		%parts, as you pushing it \\ downwards.	
    	\end{tabular}
	\end{minipage}
};
\node[mytitle, right=10pt] at (box.north west) {Board 7.2.2: Building/Fixing the Buttons on the Palm};
\end{tikzpicture}%
\end{center}

\newpage

\subsection{Building the Thumb Locking Mechanism}

\begin{table}[ht]
\centering
	\scalebox{0.97}{
	\begin{tabular}{ |c | c | c |}
		\hline
 		\multicolumn{3}{|c|}{{\bf{Parts List 7.3.1}}} \\ \hline		
		{\bf{No}} & {\bf{Part Name}} & {\bf{Qty}}\\ \hline
    		1 & toothedMechanism & 1  \\ \hline
    		2 & palmDown & 1  \\ \hline
 		\multicolumn{3}{|c|}{{\bf{Tools}}} \\ \hline
 		\multicolumn{3}{|c|}{{{ABS Glue}}} \\ \hline
    	\end{tabular}
	}
\end{table}

\begin{center}
\begin{tikzpicture}
\node [mybox] (box){%
  	\begin{minipage}[b]{0.50\linewidth}\centering
	\begin{tabular}{ c }
		
    	\end{tabular}
	\end{minipage}
	\begin{minipage}[b]{0.35\linewidth}
	\begin{tabular}{ l l}
		{\circled{1}} & {Glue the toothedMechanism}\\
		{} & {on the palmDown part.}
    	\end{tabular}
  	\end{minipage}
};
\node[mytitle, right=10pt] at (box.north west) {Board 7.3.1: Fixing the toothedMechanism on the Palm};
\end{tikzpicture}%
\end{center}

\begin{table}[h]
\centering
	\scalebox{0.97}{
	\begin{tabular}{ |c | c | c |}
		\hline
 		\multicolumn{3}{|c|}{{\bf{Parts List 7.3.2}}} \\ \hline	
		{\bf{No}} & {\bf{Part Name}} & {\bf{Qty}}\\ \hline
    		1 & lockMechanismBracket & 2  \\ \hline
    		2 & lockMechanismSupport & 1  \\ \hline
 		\multicolumn{3}{|c|}{{\bf{Material}}} \\ \hline
 		\multicolumn{3}{|c|}{{ABS Glue}} \\ \hline
    	\end{tabular}
	}
\end{table}

\begin{center}
\begin{tikzpicture}
\node [mybox] (box){%
  	\begin{minipage}[b]{0.4\linewidth}\centering
	\begin{tabular}{ l }
		
    	\end{tabular}
	\end{minipage}
	\begin{minipage}[b]{0.5\linewidth}
	\begin{tabular}{ l l }
		{\circled{1}} & {Align the lockMechanismBracket parts}\\
		{} & {with the lockMechanismSupport part.} \\ \\
		{\circled{2}} & {Glue the parts.} \\
    	\end{tabular}
  	\end{minipage}
};
\node[mytitle, right=10pt] at (box.north west) {Board 7.3.2: Building the Thumb Locking Mechanism I};
\end{tikzpicture}%
\end{center}

\newpage

\begin{table}[ht!]
\centering
	\scalebox{0.97}{
	\begin{tabular}{ |c | c | c |}
		\hline
 		\multicolumn{3}{|c|}{{\bf{Parts List 7.3.3}}} \\ \hline	
		{\bf{No}} & {\bf{Part Name}} & {\bf{Qty}}\\ \hline
		1 & Structure of Board 7.3.2 & 1  \\ \hline
		2 & toothedBlockMechanism & 1  \\ \hline
    		3 & thumbButton & 1  \\ \hline   		
 		\multicolumn{3}{|c|}{{\bf{Material}}} \\ \hline
 		\multicolumn{3}{|c|}{{ABS Glue}} \\ \hline
    	\end{tabular}
	}
\end{table}

\begin{center}
\begin{tikzpicture}
\node [mybox] (box){%
  	\begin{minipage}[b]{0.48\linewidth}\centering
	\begin{tabular}{ l }
		
    	\end{tabular}
	\end{minipage}
	\begin{minipage}[b]{0.5\linewidth}
	\begin{tabular}{ l l }
		{\circled{1}} & {Glue the thumbButton and the}\\
		{} & {toothedBlockMechanism parts}\\
		{} & {with the Structure of Board 7.3.2.}\\
    	\end{tabular}
  	\end{minipage}
};
\node[mytitle, right=10pt] at (box.north west) {Board 7.3.3: Building the Thumb Locking Mechanism II};
\end{tikzpicture}%
\end{center}

\begin{table}[ht!]
\centering
	\scalebox{0.97}{
	\begin{tabular}{ |c | c | c |}
		\hline
 		\multicolumn{3}{|c|}{{\bf{Parts List 7.3.4}}} \\ \hline		
		{\bf{No}} & {\bf{Part}} & {\bf{Qty}}\\ \hline
		1 & Strucutre of Board 7.3.3 & 1  \\ \hline
		2 & M3 Nut & 1  \\ \hline
		3 & M3 Washer & 1  \\ \hline
    		4 & M3X6 Socket Cup Screw & 1  \\ \hline
 		\multicolumn{3}{|c|}{{\bf{Tools}}} \\ \hline
		\multicolumn{3}{|c|}{{Allen Wrench}}\\ \hline		
    	\end{tabular}
	}
\end{table}

\begin{center}
\begin{tikzpicture}
\node [mybox] (box){%
  	\begin{minipage}[b]{0.50\linewidth}\centering
	\begin{tabular}{ l }
		
    	\end{tabular}
	\end{minipage}
	\begin{minipage}[b]{0.5\linewidth}
	\begin{tabular}{ l l }
		{\circled{1}} & {Align the fasteners with the}\\
		{} &  {Structure of Board 7.3.3.} \\ \\
		{\circled{2}} & {Screw the M3X6 bolt through}\\
		{} & {all fasteners.} \\
    	\end{tabular}
  	\end{minipage}
};
\node[mytitle, right=8pt] at (box.north west) {Board 7.3.4: Building the Thumb Locking Mechanism III};
\end{tikzpicture}%
\end{center}

\begin{table}[ht!]
\centering
	\scalebox{0.97}{
	\begin{tabular}{ |c | c | c |}
		\hline
 		\multicolumn{3}{|c|}{{\bf{Parts List 7.3.5}}} \\ \hline		
		{\bf{No}} & {\bf{Part}} & {\bf{Qty}}\\ \hline
		1 & thumbMovingMechanism part & 1  \\ \hline
		2 & M3X18 Set Screw & 1  \\ \hline
		3 & M3 Nut & 2  \\ \hline
		4 & Structure of Board 7.3.4 & 1  \\ \hline
    		5 & Compression Spring 3mm L, & 1 \\  & 3.5mm OD, 0.5mm WD & \\ \hline
 		\multicolumn{3}{|c|}{{\bf{Tools}}} \\ \hline
		\multicolumn{3}{|c|}{{Screwdriver}}\\ \hline
    	\end{tabular}
	}
\end{table}

\begin{center}
\begin{tikzpicture}
\node [mybox] (box){%
  	\begin{minipage}[b]{0.38\linewidth}\centering
	\begin{tabular}{ l }
		
    	\end{tabular}
	\end{minipage}
	\begin{minipage}[b]{0.5\linewidth}
	\begin{tabular}{ l l }
	    {\circled{1}} & {Align the compression spring with the}\\
	    {} & {Structure of Board 7.3.4 as shown.} \\ \\
		{\circled{2}} & {Align the two M3 nuts with the sockets of}\\
		{} & {the thumbMovingMechanism part.} \\ \\
		{\circled{3}} & {Screw the M3X18 Set Screw}\\
		{} & {through all fasteners.} \\ \\
    	\end{tabular}
  	\end{minipage}
};
\node[mytitle, right=10pt] at (box.north west) {Board 7.3.5: Building the Thumb Locking Mechanism IV};
\end{tikzpicture}%
\end{center}

\begin{table}[ht!]
\centering
	\scalebox{0.97}{
	\begin{tabular}{ |c | c | c |}
		\hline
 		\multicolumn{3}{|c|}{{\bf{Parts List 7.3.6}}} \\ \hline				
		{\bf{No}} & {\bf{Part}} & {\bf{Qty}}\\ \hline
    		1 & thumb & 1  \\ \hline
    		2 & Structure of Board 7.3.5 & 1  \\ \hline
 		\multicolumn{3}{|c|}{{\bf{Tools}}} \\ \hline
 		\multicolumn{3}{|c|}{{ABS Glue}} \\ \hline
    	\end{tabular}
	}
\end{table}

\begin{center}
\begin{tikzpicture}
\node [mybox] (box){%
  	\begin{minipage}[b]{0.50\linewidth}\centering
	\begin{tabular}{ c }
		
    	\end{tabular}
	\end{minipage}
	\begin{minipage}[b]{0.5\linewidth}
	\begin{tabular}{ l l}
		{\circled{1}} & {Center the thumb part.} \\ \\
		{\circled{2}} & {Glue the thumb with the}\\
		{} & {Structure of Board 7.3.5.}\\
    	\end{tabular}
  	\end{minipage}
};
\node[mytitle, right=10pt] at (box.north west) {Board 7.3.6: Attaching the Thumb on the Thumb Locking Mechanism};
\end{tikzpicture}%
\end{center}

\newpage 

\subsection{Tendon Routing System/Servo Base Assembly \& Mount On the Palm}

\begin{table}[ht!]
\centering
	\scalebox{0.9}{
	\begin{tabular}{ |c | c | c |}
		\hline
		\multicolumn{3}{|c|}{{\textbf{Parts List 7.4.1}}}\\ \hline
		{\bf{No}} & {\bf{Part Name}} & {\bf{Qty}}\\ \hline
    		1 & M3 Nut & 2  \\ \hline
    		2 & M3X12 Set Screw & 1  \\ \hline
    		3 & basePulleyInsidePalm & 2  \\ \hline
    		4 & M3 Washer & 2  \\ \hline
    		5 & V-Grooved Sealed Ball Bearing & 1  \\ \hline
 		\multicolumn{3}{|c|}{{\bf{Tools}}} \\ \hline
		\multicolumn{3}{|c|}{{Long-Nose Pilers with Side-Cutting}}\\ \hline
		\multicolumn{3}{|c|}{{Screwdriver}}\\ \hline
    	\end{tabular}
	}
\end{table}

\begin{center}
\begin{tikzpicture}
\node [mybox] (box){%
  	\begin{minipage}[b]{0.5\linewidth}\centering
	\begin{tabular}{ l }
		
    	\end{tabular}
	\end{minipage}
	\begin{minipage}[b]{0.5\linewidth}
	\begin{tabular}{ l l }
		{\circled{1}} & {Align the two M3 nuts with the sockets of}\\
		{} & {basePulleyInsidePalm parts.} \\ \\
		{\circled{2}} & {Align the M3 Nuts, M3 Washers and pulley}\\
		{} & {as shown.} \\ \\
		{\circled{3}} & {Screw the M3X12 Set Screw through}\\
		{} & {all fasteners.} \\
    	\end{tabular}
  	\end{minipage}
};
\node[mytitle, right=10pt] at (box.north west) {Board 7.4.1: Building the Tendon Routing Pulley Base I};
\end{tikzpicture}%
\end{center}

\begin{table}[ht!]
\centering
	\scalebox{0.9}{
	\begin{tabular}{ |c | c | c |}
		\hline
 		\multicolumn{3}{|c|}{{\textbf{Parts List 7.4.2}}} \\ \hline		
		{\bf{No}} & {\bf{Part Name}} & {\bf{Qty}}\\ \hline
    		1 & M3 Nut & 1  \\ \hline
    		2 & M3 Washer & 2  \\ \hline
    		3 & V-Grooved Sealed Ball Bearing & 1  \\ \hline
    		4 & supportPulleyPalmUpAssem & 1  \\ \hline
    		5 & M3X10 Socket Cup Screw & 1  \\ \hline
 		\multicolumn{3}{|c|}{{\bf{Tools}}} \\ \hline
 		\multicolumn{3}{|c|}{{{Long-Nose Pilers with Side-Cutting}}} \\ \hline
 		\multicolumn{3}{|c|}{{{Allen Wrench}}} \\ \hline
    	\end{tabular}
	}
\end{table}

\begin{center}
\begin{tikzpicture}
\node [mybox] (box){%
  	\begin{minipage}[b]{0.50\linewidth}\centering
	\begin{tabular}{ l }
		
    	\end{tabular}
	\end{minipage}
	\begin{minipage}[b]{0.5\linewidth}
	\begin{tabular}{ l l }
		{\circled{1}} & {Align the M3 nut with the socket}\\
		{} & {of the structure of Board 7.2.2.} \\ \\
		{\circled{2}} & {Align the M3 Washers,}\\
		{} &  {the supportPulleyPalmUpAssem part}\\
		{} & {and the pulley as shown.} \\ \\
		{\circled{3}} & {Screw the M3X6 bolt through}\\
		{} &  {all fasteners.} \\
    	\end{tabular}
  	\end{minipage}
};
\node[mytitle, right=10pt] at (box.north west) {Board 7.4.2: Building the Support of the Pulley Base};
\end{tikzpicture}%
\end{center}

\begin{table}[ht!]
\centering
	\scalebox{0.97}{
	\begin{tabular}{ |c | c | c |}
		\hline
 		\multicolumn{3}{|c|}{{\bf{Parts List 7.4.3}}} \\ \hline		
		{\bf{No}} & {\bf{Part Name}} & {\bf{Qty}}\\ \hline
    		1 & Structure of Board 7.4.2 & 1  \\ \hline
    		2 & M2X10 Machine Screw & 4  \\ \hline
    		3 & Plastic Spacer 4mm & 4  \\ \hline
    		4 & baseHerkulex part & 1  \\ \hline
    		5 & M2 Nut & 4  \\ \hline
 		\multicolumn{3}{|c|}{{\bf{Tools}}} \\ \hline
 		\multicolumn{3}{|c|}{{{Screwdriver}}} \\ \hline
    	\end{tabular}
	}
\end{table}

\begin{center}
\begin{tikzpicture}
\node [mybox] (box){%
  	\begin{minipage}[b]{0.45\linewidth}\centering
	\begin{tabular}{ l }
		
    	\end{tabular}
	\end{minipage}
	\begin{minipage}[b]{0.5\linewidth}
	\begin{tabular}{ l l }
		{\circled{1}} & {Align the four M2 nuts with}\\
		{} &  {the baseHerkulex part.} \\ \\
		{\circled{2}} & {Align the baseHerkulex part,}\\
		{} & {the spacer and the M2X10 bolts}\\
		{} & {as shown.} \\ \\
		{\circled{3}} & {Screw the four M2X10 bolts through}\\
		{} & {all fasteners.} \\
    	\end{tabular}
  	\end{minipage}
};
\node[mytitle, right=10pt] at (box.north west) {Board 7.4.3: Building the Support for the Servo Base};
\end{tikzpicture}%
\end{center}

\begin{table}[ht!]
\centering
	\scalebox{0.97}{
	\begin{tabular}{ |c | c | c |}
		\hline
 		\multicolumn{3}{|c|}{{\bf{Parts List 7.4.4}}} \\ \hline		
		{\bf{No}} & {\bf{Part Name}} & {\bf{Qty}}\\ \hline
    		1 & low fricion tubes & --  \\ \hline
    		2 & Dyneema & --  \\ \hline
    		3 & barIndexMiddle & 1  \\ \hline
    		4 & barRingPinky & 1  \\ \hline
    		5 & mainBar & 1  \\ \hline
    		6 & Structure of Board 7.4.3 & 1  \\ \hline
 		\multicolumn{3}{|c|}{{\bf{Tools}}} \\ \hline
 		\multicolumn{3}{|c|}{{{Long Needles}}} \\ \hline
 		\multicolumn{3}{|c|}{{{Scissors}}} \\	 \hline				
    	\end{tabular}
	}
\end{table}

\begin{center}
\begin{tikzpicture}
\node [mybox] (box){%
  	\begin{minipage}[b]{0.50\linewidth}\centering
	\begin{tabular}{ c }
		
    	\end{tabular}
	\end{minipage}
	\begin{minipage}[b]{0.5\linewidth}
	\begin{tabular}{ l l }
		{\circled{1}} & {Tie the Index and Middle Tendons}\\
		{} & {on the barIndexMiddle part.} \\ \\
		{\circled{2}} & {Tie the Ring and Pinky Tendons}\\
		{} & {on the barRingPinky part.} \\ \\
		{\circled{3}} & {Connect the barRingPinky}\\
		{} & {and barIndexMiddle tendons}\\
		{} & {with the mainBar part as shown.} \\
    	\end{tabular}
  	\end{minipage}
};
\node[mytitle, right=10pt] at (box.north west) {Board 7.4.4: Connecting the Whiffletree Bars with the Dyneema Tendons};
\end{tikzpicture}%
\end{center}

\begin{table}[ht!]
\centering
  	\begin{minipage}[b]{0.50\linewidth}\centering
	\scalebox{0.97}{
	\begin{tabular}{ |c | c | c |}
		\hline
 		\multicolumn{3}{|c|}{{\bf{Parts List 7.4.5}}} \\ \hline				
		{\bf{No}} & {\bf{Part}} & {\bf{Qty}}\\ \hline
    		1 & M3 nut & 1  \\ \hline
    		2 & basePulleyInsidePalm & 2  \\ \hline
    	\end{tabular}
	}
	\end{minipage}
	\hspace{0.5cm}	
\end{table}

\begin{center}
\begin{tikzpicture}
\node [mybox] (box){%
  	\begin{minipage}[b]{0.5\linewidth}\centering
	\begin{tabular}{ l }
		
    	\end{tabular}
	\end{minipage}
	\begin{minipage}[b]{0.5\linewidth}
	\begin{tabular}{ l  l }
		{\circled{1}} & {Place the M3 nut in the socket}\\
		{} & {of basePulleyInsidePalm part.} \\ \\
		{\circled{2}} & {Repeat step \circled{1} for a second part.} \\
    	\end{tabular}
  	\end{minipage}
};
\node[mytitle, right=10pt] at (box.north west) {Board 7.4.5: Building the Support of the Pulley Base II};
\end{tikzpicture}%
\end{center}

\begin{table}[ht!]
\centering
  	\begin{minipage}[b]{0.50\linewidth}\centering
	\scalebox{0.97}{
	\begin{tabular}{ |c | c | c |}
		\hline
	 	\multicolumn{3}{|c|}{{\bf{Parts List 7.4.6}}} \\ \hline			
		{\bf{No}} & {\bf{Part}} & {\bf{Qty}}\\ \hline
    		1 & Structure of Board 7.4.1 & 1  \\ \hline
    		2 & Structure of Board 7.4.4 & 1  \\ \hline
    		3 & Structure of Board 7.4.5 & 2  \\ \hline
    	\end{tabular}
	}
	\end{minipage}
	\hspace{0.5cm}
\end{table}

\begin{center}
\begin{tikzpicture}
\node [mybox] (box){%
  	\begin{minipage}[b]{0.50\linewidth}\centering
	\begin{tabular}{ l }
		
    	\end{tabular}
	\end{minipage}
	\begin{minipage}[b]{0.4\linewidth}
	\begin{tabular}{ l l }
		{\circled{1}} & {Align part 1 with the}\\
		{} & {socket of part 2 as shown.} \\ \\
		{\circled{2}} & {Align part 3 with the}\\
		{} & {socket of part 2 as shown.} \\
    	\end{tabular}
  	\end{minipage}
};
\node[mytitle, right=10pt] at (box.north west) {Board 7.4.6: Attaching the Support of the Tendon Routing Base on the Palm};
\end{tikzpicture}%
\end{center}

\begin{table}[ht!]
	\centering
	\scalebox{0.9}{
		\begin{tabular}{ |c | c | c |}
			\hline
			\multicolumn{3}{|c|}{{\bf{Parts List 7.4.7}}} \\ \hline		
			{\bf{No}} & {\bf{Part Name}} & {\bf{Qty}}\\ \hline
			1 & palmDown & 1  \\ \hline
			2 & palmUp & 1  \\ \hline
			3 & M3X16 Socket Cup Screw & 1  \\ \hline
			4 & M3 Washer & 2  \\ \hline
			5 & M3 Nut & 1  \\ \hline
			6 & Plastic spacer 4mm & 1  \\ \hline	
			\multicolumn{3}{|c|}{{\bf{Tools}}} \\ \hline
			\multicolumn{3}{|c|}{{{Allen Wrench}}} \\ \hline		
		\end{tabular}
	}
\end{table}

\begin{center}
	\begin{tikzpicture}
	\node [mybox] (box){%
		\begin{minipage}[b]{0.50\linewidth}\centering
		\begin{tabular}{ l }
		
		\end{tabular}
		\end{minipage}
		\begin{minipage}[b]{0.4\linewidth}
		\begin{tabular}{ l l }
		{\circled{1}} & {Align palmUp with palmDown.} \\ \\
		{\circled{2}} & {Screw the M3X16 bolt through}\\
		{} &  {all fasteners as shown.} \\ \\
		{\circled{!}} & {The gap between palmUp and}\\
		{} & {palmDown parts should be 4mm.} \\
		\end{tabular}
		\end{minipage}
	};
	\node[mytitle, right=10pt] at (box.north west) {Board 7.4.7: Attaching the Upper and Lower Palm Parts};
	\end{tikzpicture}%
\end{center}

\newpage

\begin{table}[ht!]
	\centering
	\scalebox{0.97}{
		\begin{tabular}{ |c | c | c |}
			\hline
			\multicolumn{3}{|c|}{{\bf{Parts List 7.4.8}}} \\ \hline		
			{\bf{No}} & {\bf{Part Name}} & {\bf{Qty}}\\ \hline
			1 & M3 Nut & 4  \\ \hline
			2 & supportPulley1 part & 2  \\ \hline
			3 & Plastic Spacer 4mm & 4  \\ \hline
			4 & M3X18 Set Screw & 2  \\ \hline
			5 & V-Grooved Sealed Ball Bearing & 2  \\ \hline	
			\multicolumn{3}{|c|}{{\bf{Tools}}} \\ \hline
			\multicolumn{3}{|c|}{{{Screwdriver}}} \\ \hline		
		\end{tabular}
	}
\end{table}

\begin{center}
	\begin{tikzpicture}
	\node [mybox] (box){%
		\begin{minipage}[b]{0.50\linewidth}\centering
		\begin{tabular}{ l }
		
		\end{tabular}
		\end{minipage}
		\begin{minipage}[b]{0.5\linewidth}
		\begin{tabular}{ l l }
		{\circled{1}} & {Align the 4 M3 Nuts with}\\
		{} & {the sockets of supportPulley1.}\\ \\
		{\circled{2}} & {Align the 4 Spacers with}\\
		{} &  {the pulleys.} \\ \\
		{\circled{3}} & {Screw the M3X18 Set Screws}\\
		{} & {on all fasteners.} \\
		\end{tabular}
		\end{minipage}
	};
	\node[mytitle, right=10pt] at (box.north west) {7.4.8: Building the Tendon Routing Pulley Base II};
	\end{tikzpicture}%
\end{center}

\newpage

\subsection{Attaching the Thumb Locking Mechanism and Tendon Routing on the Palm}

\begin{table}[ht!]
	\centering
	\scalebox{0.97}{
		\begin{tabular}{ |c | c | c |}
			\hline
			\multicolumn{3}{|c|}{{\bf{Parts List 7.5.1}}} \\ \hline		
			{\bf{No}} & {\bf{Part Name}} & {\bf{Qty}}\\ \hline
			1 & Structure of Board 7.4.7 & 1  \\ \hline
			2 & Structure of Board 7.3.4 & 1  \\ \hline
			3 & M3X30 Set Screw & 1  \\ \hline
			4 & V-Grooved Sealed Ball Bearing & 1  \\ \hline
			5 & M3 Nut & 2  \\ \hline	
			\multicolumn{3}{|c|}{{\bf{Tools}}} \\ \hline
			\multicolumn{3}{|c|}{{{Screwdriver}}} \\ \hline		
		\end{tabular}
	}
\end{table}

\begin{center}
	\begin{tikzpicture}
	\node [mybox] (box){%
		\begin{minipage}[b]{0.50\linewidth}\centering
		\begin{tabular}{ l }
		
		\end{tabular}
		\end{minipage}
		\begin{minipage}[b]{0.4\linewidth}
		\begin{tabular}{ l l }
		{\circled{1}} & {Align the pulley to part 2.} \\ \\
		{\circled{2}} & {Align part 2 with part 1 as shown.} \\ \\
		{\circled{3}} & {Screw the M3X30 Set Screw}\\
		{} &  {on all fasteners.} \\
		\end{tabular}
		\end{minipage}
	};
	\node[mytitle, right=10pt] at (box.north west) {Board 7.5.1: Attaching the Thumb Locking Mechanism on its Palm Base};
	\end{tikzpicture}%
\end{center}

\begin{table}[ht!]
	\centering
	\scalebox{0.97}{
		\begin{tabular}{ |c | c | c |}
			\hline
			\multicolumn{3}{|c|}{{\bf{Parts List 7.5.2}}} \\ \hline		
			{\bf{No}} & {\bf{Part Name}} & {\bf{Qty}}\\ \hline
			1 & Structure of Board 7.5.1 & 1  \\ \hline
			2 & Structure of Board 7.4.8 & 1  \\ \hline		
		\end{tabular}
	}
\end{table}

\begin{center}
	\begin{tikzpicture}
	\node [mybox] (box){%
		\begin{minipage}[b]{0.5\linewidth}\centering
		\begin{tabular}{ c }
		
		\end{tabular}
		\end{minipage}
		\begin{minipage}[b]{0.5\linewidth}
		\begin{tabular}{ l l }
		{\circled{1}} & {Attach part 2 on part 1.} \\
		\end{tabular}
		\end{minipage}
	};
	\node[mytitle, right=10pt] at (box.north west) {Board 7.5.2: Attaching the Thumb Tendon Routing Base on the Palm};
	\end{tikzpicture}%
\end{center}

\begin{table}[ht!]
	\centering
	\scalebox{0.97}{
		\begin{tabular}{ |c | c | c |}
			\hline
			\multicolumn{3}{|c|}{{\bf{Parts List 7.5.3}}} \\ \hline		
			{\bf{No}} & {\bf{Part Name}} & {\bf{Qty}}\\ \hline
			1 & Dyneema & --  \\ \hline
			2 &  V-Grooved Sealed Ball Bearing & 2  \\ \hline
			\multicolumn{3}{|c|}{{\bf{Tools}}} \\ \hline
			\multicolumn{3}{|c|}{{{Long Needles}}} \\ \hline		
		\end{tabular}
	}
\end{table}

\begin{center}
	\begin{tikzpicture}
	\node [mybox] (box){%
		\begin{minipage}[b]{0.50\linewidth}\centering
		\begin{tabular}{ c }
		
		\end{tabular}
		\end{minipage}
		\begin{minipage}[b]{0.4\linewidth}
		\begin{tabular}{ l l }
		{\circled{1}} & {Pass the thumb tendon around}\\
		{} & {pulley-part 2.} \\ \\
		{\circled{!}} & {Long needles can be used}\\
		{} & {to simplify the process.} \\
		\end{tabular}
		\end{minipage}
	};
	\node[mytitle, right=10pt] at (box.north west) {Board 7.5.3: Passing the thumb Tendon around Tendon Routing Pulley 1};
	\end{tikzpicture}%
\end{center}

\newpage

\begin{table}[ht!]
	\centering
	\scalebox{0.97}{
		\begin{tabular}{ |c | c | c |}
			\hline
			\multicolumn{3}{|c|}{{\bf{Parts List 7.5.4}}} \\ \hline		
			{\bf{No}} & {\bf{Part Name}} & {\bf{Qty}}\\ \hline
			1 & Dyneema & --  \\ \hline
			2 &  V-Grooved Sealed Ball Bearing & 2  \\ \hline
			\multicolumn{3}{|c|}{{\bf{Tools}}} \\ \hline
			\multicolumn{3}{|c|}{{{Long Needles}}} \\ \hline		
		\end{tabular}
	}
\end{table}

\begin{center}
	\begin{tikzpicture}
	\node [mybox] (box){%
		\begin{minipage}[b]{0.50\linewidth}\centering
		\begin{tabular}{ l }
		
		\end{tabular}
		\end{minipage}
		\begin{minipage}[b]{0.4\linewidth}
		\begin{tabular}{ l l }
		{\circled{1}} & {Pass the thumb tendon around}\\
		{} & {pulley-part 2.} \\ \\
		{\circled{!}} & {Long needles can be used}\\
		{} & {to simplify the process.} \\	\\ \\ \\
		\end{tabular}
		\end{minipage}
	};
	\node[mytitle, right=10pt] at (box.north west) {Board 7.5.4: Passing the thumb Tendon around Tendon Routing Pulley 2};
	\end{tikzpicture}%
\end{center}

\newpage

\subsection{Attaching the Base Flange on the Hand}

\begin{table}[ht!]
	\centering
	\scalebox{0.97}{
		\begin{tabular}{ |c | c | c |}
			\hline
			\multicolumn{3}{|c|}{{\bf{Parts List 7.6.1}}} \\ \hline		
			{\bf{No}} & {\bf{Part Name}} & {\bf{Qty}}\\ \hline
			1 & Prosthetic Hand & 1  \\ \hline
			2 &  flangePlate part & 1  \\ \hline
			3 &  M3X20 Socket Cup Screw & 2  \\ \hline
			4 &  dovetailFemale part & 1  \\ \hline
			\multicolumn{3}{|c|}{{\bf{Tools}}} \\ \hline
			\multicolumn{3}{|c|}{{{Allen Wrench}}} \\ \hline	
			\multicolumn{3}{|c|}{{{ABS Glue}}} \\ \hline	
		\end{tabular}
	}
\end{table}

\begin{center}
	\begin{tikzpicture}
	\node [mybox] (box){%
		\begin{minipage}[b]{0.5\linewidth}\centering
		\begin{tabular}{ l }
		
		\end{tabular}
		\end{minipage}
		\begin{minipage}[b]{0.37\linewidth}
		\begin{tabular}{ l l }
		{\circled{1}} & {Glue the flangePlate}\\
		{} & {on the dovetailFemale.} \\ \\
		{\circled{2}} & {Place the flangePlate}\\
		{} & {on the Hand.} \\ \\
		{\circled{3}} & {Screw M3X20 bolts through}\\
		{} & {the M3 Nuts of the Hand.} \\
		\end{tabular}
		\end{minipage}
	};
	\node[mytitle, right=10pt] at (box.north west) {Board 7.6.1: Attaching the Base Flange on the Hand Palm};
	\end{tikzpicture}%
\end{center}

\subsection{Hand is Assembled}

{\large Congratulations you have created an affordable, anthropomorphic, personalized, light-weight prosthetic hand!}

\begin{center}
   \fbox{}
\end{center}

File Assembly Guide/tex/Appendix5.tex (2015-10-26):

\section{Final Results}

{\large Congratulations you have created an Affordable, Anthropomorphic, Light-Weight Prosthetic Hand!}

\vspace{1in}

\begin{center}
   \fbox{}
\end{center}

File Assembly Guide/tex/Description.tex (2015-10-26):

\section{Introduction}

\indent This technical report is intended to serve as a step by step tutorial for the replication of a prosthetic hand \cite{Kontoudis2015IROS} developed by the \href{www.openbionics.org}{OpenBionics (www.openbionics.org)} initiative \cite{Liarokapis2014ASURRW}. Based on a previous design for the OpenBionics robotic hands \cite{Zisimatos2014IROS}, the prosthetic hand was developed to be affordable, light-weight and intrinsically-compliant. The proposed design is also structurally and kinematically anthropomorphic. In particular, its sizing is parametrically determined in an anthropomorphic fashion, according to data provided by hand anthropometry studies \cite{BuchholzErgonomics1992}, allowing for personalization and adjustment to the needs of each individual. Moreover, its kinematic model is derived by incorporating an index of Anthropomorphism \cite{Liarokapis2013ICRA} in the design optimization process. Finally, the prosthetic hand bears a novel differential mechanism based on the \textit{whiffletree} or \textit{seesaw} mechanism that allows the user to switch between various postures using a single actuator. Postures and gestures selection is easy and intuitive, through the use of simple locking buttons that can independently block the motion of each finger. The proposed hands can be easily fabricated using low-cost, off-the-shelf materials and rapid prototyping techniques. 

In the following sections, we describe in detail all the necessary steps for the replication of the proposed prosthetic hand. In order to facilitate the fabrication for non-expert users, effort has been devoted to utilize off-the-shelf materials and equipment that can be easily found in hardware stores around the world.

\section{Prosthetic Hand Design}

In this section we present the prosthetic hand design. The hand is underactuated as all five fingers are controlled with a single actuator which is mounted on the palm. The transmission is achieved with tendons driven through low-friction tubes. A differential mechanism facilitates the execution of multiple postures and gestures with the single actuator. 

\subsection{Anthropomorphism}

Recently, Liarokapis et al. \cite{Liarokapis2013ICRA} formalized an index of anthropomorphism for quantifying the humanlikeness of robot hands in terms of motion capabilities and morphology. The index was defined as the weighted sum of workspace similarity subscores. These subscores were derived from comparisons between the robot hand and a human hand reference. Human hand anthropometry studies \cite{BuchholzErgonomics1992} were used to define the representative human hand model. The proposed index of anthropomorphism can be used in order to assess the humanlikeness of existing robot hands, or as an optimization criterion for designing a new generation of robot and prosthetic hands. We argue that anthropomorphism not only results to more aesthetically superior artifacts but also to a better performance in everyday life grasping and manipulation tasks. This conclusion was based on the simple observation that the objects surrounding us have been crafted according to the design and the capabilities of the human hand. Therefore, structurally and kinematically anthropomorphic artificial hands may be more well suited to execute a wide variety of everyday life tasks. 

Based on this observation, we used the index of Anthropomorphism to extract specifications for the design of our anthropomorphic prosthetic hand. In particular, we optimized for anthropomorphism with respect to the finger phalanges lengths and the positions/orientations of the finger base frames. The human hand reference was extracted from parametric models \cite{BuchholzErgonomics1992} that only require two human hand parameters: 1) the hand length (HL) and 2) hand breadth (HB). 

Finally, the extracted finger base frames orientations were further optimized to allow for a satisfactory Kapandji score \cite{Kapandji}. The Kapandji score is a tool that is widely used by physicians in order to evaluate a patient's thumb opposition capability by asking the subject to use their thumb to touch a set of different palm locations. Based on the locations reached, a score indicative of the thumb's opposition dexterity is determined by the Kapandji scale. This tool has lately found applications in robot hand design \cite{GrebensteinThesis}. Inspired by the aforementioned study, we used the Kapandji score as a criterion for determining the hand's kinematics in order for the thumb fingertip to be able to make contact with 1) the base frames of the remaining four fingers and 2) the tips of the index and pinky fingers. 

%\ref{baseFrames}.

%as shown in Fig. \ref{fingertips}.

\subsection{Finger Design}

Each one of the index, middle, ring and pinky fingers consists of three phalanges and three rotational Degrees of Freedom (DoF) for flexion/extension, while the thumb consists of two phalanges and two rotational DoF for flexion/extension and one rotational DoF for abduction/adduction. All joints of the fingers are flexure joints based on elastomer materials (silicone or polyurethane sheets), the sizing of which was determined empirically to achieve both a lightweight structure and a force range that is adequate for everyday life tasks \cite{DollarAR2005}. In terms of functionality, the aforementioned finger actuation and transmission is bioinspired, in the sense that it structurally replicates the flexion/extension motions of the human fingers. More specifically, the use of elastomer materials on the joints implements the passive extension, while cables (Dyneema fishing line) driven through low-friction tubes implement the flexion. Finally, in order to enhance stability through force impact absorption and increased friction at the contacts \cite{deformableciocarlie2005}, we covered the fingertips with: 1) deformable sponge-like tape , 2) rubber tape and 3) anti-slip tape.

\subsection{Palm}

The palm consists of two parallel planes that can be made out of Plexiglas (acrylic) or ABS (depending on the manufacturing technique used) and which  accommodate: 1) the finger base frames, 2) the thumb mechanism, 3) the selectively lockable differential mechanism (i.e., the whiffletree and the buttons) and 4) the actuator base. In the following sections we describe in detail the thumb locking mechanism and the selectively lockable differential mechanism.

\subsubsection{Thumb Locking Mechanism}

For the thumb we use a selectively lockable toothed mechanism that can implement 9 different opposition configurations as depicted in Fig. \ref{thumb}. These configurations were selected to allow the efficient execution of the Kapandji test \cite{Kapandji} and to allow also the user to switch among different grasping postures (e.g., pinch grasp, power grasp, key grasp etc.). The proposed one DoF thumb mechanism serves as a simple alternative to the mechanically complex three DoF human thumb. The proposed mechanism is completely stiff when it is locked, in contrast to the friction based mechanisms \cite{Baril} that are affected by torsional forces that are inherent in dynamic/unstructured environments (these forces can result to large, uncontrolled displacements of the thumb for these mechanisms). The thumb tendon is terminated to an appropriate servo pulley. Small motor angular displacements are required for the finger to be actuated. Finally, the diameters of the pulleys were optimized for the Kapandji test \cite{Kapandji}.

\begin{figure}[h]
%\setlength{\belowcaptionskip}{-8pt}
%\setlength{\abovecaptionskip}{-6pt}
\begin{center}

\end{center}
\caption{The thumb mechanism consists of the red and golden parts. The red parts are mounted in appropriate slots on the robot palm to facilitate installation of the thumb mechanism. The golden parts are: 1) a pulley that routes the thumb tendon to the back of the hand and 2) the toothed, selectively lockable mechanism that allows adjustment of thumb's opposition. The robot thumb can be passively positioned by the user, in 9 discrete configurations.} 
\label{thumb}
\end{figure}

\subsubsection{A Selectively Lockable Differential Mechanism}

A selectively lockable differential mechanism connects the actuator with the tendons of each finger. The mechanism is a variation of the whiffletree \cite{Birglen}. The whiffletree consists of three bars: one bar connecting the index and middle fingers (bar 1), one bar connecting the ring and pinky fingers (bar 2) and the main bar that connects bar 1 and bar 2, as depicted in Fig. \ref{differential}. The top two bars of the whiffletree bear 2 slots each, which allow for selective independent locking of all fingers upon pressing of corresponding buttons that are mounted on the top of the palm. Intuitively, when each button is pressed, the corresponding bar slot is filled and the corresponding finger's motion is blocked. Therefore, switching among different hand postures is easy. A total of $2^4=16$ different finger combinations can be implemented and when they are combined with the 9 discrete positions of the thumb, they result to 144 distinct postures that can be achieved with a single actuator. The differential mechanism is depicted in Fig. \ref{differential} and the locking buttons in Figs. \ref{palm} and \ref{RobotHandViews}.

\begin{figure}[h]
\begin{center}

\end{center}
\caption{Inner side of the palm. The three bars of the proposed whiffletree are depicted with red color. The holes of the upper two bars are filled by the elongated parts of the corresponding buttons, constraining the motion of different fingers. In this instance the motion of the index and pinky fingers is constrained, resulting to a change at the inclination of the differential mechanism finger bars.} 
\label{differential}
\end{figure}

\subsection{Fabrication Techniques and Personalized Design}

All files (CAD files, codes) required for the replication and control of the proposed robot hands, are available for download through the OpenBionics initiative \cite{Liarokapis2014ASURRW} website at the following URL:
\begin{center}{\small{\url{http://www.openbionics.org}}}\end{center} 

 The proposed design is essentially 2D and can be replicated with various fabrication techniques. In particular, we provide 3D models (.stl files) that can be used for fabrication with rapid prototyping techniques such as 3D printing and 2D models (.dwg, .dxf and other CAD files) that can be used for fabrication with laser cutting machines or other standard machining tools. The proposed hands are made out of off-the-shelf, low-cost materials. All required materials can be easily found in hardware stores around the world. 

 \begin{figure}[h]
\begin{center}
\begin{tabular}[50]{ c c }
&
\\
{{a) thumb mechanism}} & {{b) servo base}}\\
\end{tabular}
\end{center}
\caption{Subfigure a) depicts the thumb mechanism in red and golden colors. Subfigure b) depicts the servo base of the HerkuleX servo motor in red. In both subfigures the buttons that implement the differential tree locking are denoted with black color.} 
\label{palm}
\end{figure} 

For reference, we provide the finger design parameters for a prosthetic hand with length 19 cm in Table \ref{fingerparameters}, while other complementary features are reported in Table \ref{handcharacteristics}. It should be pointed out that both the weight and the cost of the proposed hand design are significantly low, 300 g and $<$200 USD respectively. 

\begin{table}[ht!]
\caption{Finger characteristics for a robot hand with length 19cm} \label{fingerparameters}
\begin{center}
\begin{tabular}[50]{ c c c c c }
{\it{Finger}} & {\it{Weight}} & {\it{Length}} & {\it{Breadth}} & {\it{Width}}\\
\hline
{Index} & {30 g} & {88 mm} & {16.2 mm} & {15 mm}\\
{Middle} & {30 g} & {98 mm} & {16.2 mm} & {15 mm}\\
{Ring} & {30 g} & {95 mm} & {16.2 mm} & {15 mm}\\
{Pinky} & {25 g} & {76 mm} & {16.2 mm} & {15 mm}\\
{Thumb} & {20 g} & {68 mm} & {16.2 mm} & {15 mm}\\
\end{tabular}
\end{center}
\end{table} 

\begin{table}[ht!]
\caption{Hand characteristics} \label{handcharacteristics}
\begin{center}
\begin{tabular}[50]{ c c c c c }
{\it{Cost}} &  {\it{Weight}} & {\it{Length}} & {\it{Breadth}} & {\it{Width}}\\
$<$ 200 USD & 300 g & 190 mm & 90 mm & 62.50 mm 
\end{tabular}
\end{center}
\end{table} 

 \begin{figure}[ht]
\centering
\begin{tabular}[50]{ c c c c }
{\it{Front}} & {\it{Side 1}} & {\it{Side 2}} & {\it{Back}}\\
&
&
&
\\
\end{tabular}
\caption{Different views of the prosthetic hand developed.} 
\label{RobotHandViews}
\end{figure} 

\section{Results \& Experiments}

The performance capabilities of the proposed design have already been validated with extensive experimental paradigms that include: 1) grasping of a wide range of everyday life objects, 2) execution of a series of daily living tasks. For the experiments, we used an Arduino Micro platform \cite{Arduino} to control the HerkuleX DRS0201 servo motor, a custom made PCB module that connects the arduino platform with the servo motor and the ROS package (written in Python) that we created within the context of the OpenBionics initiative (available at \url{https://github.com/OpenBionics}). In the following sections we evaluate the performance of the proposed prosthetic hands.

\subsection{Force Exertion Capability}

Fig. \ref{forcedisplacement} contains diagrams demonstrating the relationships between the linear displacement of the tendon and the force applied at the fingertips, with and without finger blocking, for various hand postures. This can be useful for performing precision grasps, since blocking a subset of fingers leads to increased force transmission for the remaining free fingers.

\begin{figure}[h]
\centering
\begin{tabular}{ c c c }
 &
 &
\\ 
 & 

\end{tabular}
\caption{Relationship between tendon displacement and finger forces for various postures.} 
\label{forcedisplacement}
\end{figure}

\subsection{Implementing Various Grasping Postures and Common Gestures}

The efficacy of the selectively lockable differential mechanism was validated through a plethora of experiments.  The user was pressing the locking buttons to achieve different postures. This functionality is not only important for grasping (where the user is able to choose a preferred grasping strategy / posture), but also for: 1) implementing specific gestures (e.g., making the peace sign or showing a number), 2) reaching for an object located at a narrow space (task that might require less than five fingers), or 3) execute non-prehensile manipulation tasks (e.g., press a button or move a slider on a console). Figs. \ref{Locked} and \ref{Free} depict various postures, achieved by pressing different sets of buttons. 

\begin{figure}[ht]
\begin{center}
\scalebox{0.95}{
\begin{tabular}[50]{ c c c c }
{\it{Index}} & {\it{Middle}} & {\it{Ring}} & {\it{Pinky}}\\
&
& 
&
\\
\end{tabular}
}
\end{center}
\caption{Four different postures are depicted. All fingers except one are closing. The locked finger can be used to: 1) press buttons, 2) to reach something in narrow spaces, 3) to implement specific gestures or 4) to execute non-prehensile manipulation tasks (e.g., moving a slider).} 
\label{Locked}
\end{figure} 

\begin{figure}[ht]
\begin{center}
\begin{tabular}{ c c c c }
{\it{M, R, P}} & {\it{I, M}} & {\it{I, M, P}} & {\it{I, P}}\\
&
& 
&
\\
\end{tabular}
\end{center}
\caption{Four different postures are depicted. The differential mechanism allows for different grasping postures and hand gestures to be achieved. With the letters I, M, R and P we denote that motion of the index, middle, ring and pinky finger respectively, is constrained.} 
\label{Free}
\end{figure}

\subsection{Grasping Everyday Life Objects}

The actual grasping capabilities of the hand were tested through a set of experiments during which the user grasped a wide range of everyday life objects, to execute common daily living activities. For these experiments we used 1) a mug, 2) a soap, 3) a magazine, 4)  a marker, 5) a pair of glasses, 6) a large rectangular box, 7) a glass cleaner spray, 8) a 1.5L bottle of water, 9) a glass of water and 10) a spoon. Regarding the daily living tasks, the hand is used: 1) to serve water from a 1.5L bottle to a glass, 2) to stir the water inside the glass with a spoon and 3) to position a series of tools to their cases and put them inside a rectangular box. Instances of the conducted experiments are displayed in Fig. \ref{Experiments}. All experiments were recorded and the video can be found (in HD quality), at the following URL: 
\begin{center}{\small{\url{http://www.openbionics.org/videos/}}}\end{center}

More details about the experiments and the possible applications, can be found in \cite{Kontoudis2015IROS}, as well as at the official website of the OpenBionics initiative:

\begin{center}
{\url{http://www.openbionics.org}}
\end{center} 

\begin{figure}[ht!]
\centering
\scalebox{0.98}{
\begin{tabular}[50]{ c c c c }
{\it{Mug}} & {\it{Marker}} & {\it{Sunglasses}} & {\it{Bottle}}\\
&
&
&
\\
\end{tabular}
}
\caption{Images from the experiments conducted. Five different everyday life objects are grasped in order to execute different tasks: 1) a coffee mug is grasped from the handle in order to drink from it, 2) a marker is grasped in order to write, 3) a pair of glasses are picked up and 4) a 1.5L bottle is grasped in order to serve water.} 
\label{Experiments}
\end{figure} 

\newpage

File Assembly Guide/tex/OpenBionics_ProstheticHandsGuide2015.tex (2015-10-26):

\documentclass[a4paper]{report}

\usepackage[top=3cm, bottom=3cm, left=3cm, right=3cm]{geometry}

\usepackage{hyperref}
\usepackage{url}
\usepackage{cite}

\usepackage[usenames,dvipsnames]{xcolor}

\usepackage{tikz}
\tikzset{
  box/.style={
    minimum width=\pagewidth,
    draw,
    rounded corners,
    rectangle
  },
}
\usetikzlibrary{shapes,snakes}
\usepackage{amsmath,amssymb}

\usepackage{float}
\usepackage{wrapfig}

\usepackage[english]{babel}
\usepackage{array}
\usepackage{caption}
\usepackage{subcaption}
\usepackage{graphicx}
\usepackage{sidecap}
\usepackage{float}
\usepackage{varwidth}

% section wise numbering of figures etc..
\usepackage{chngcntr}
\counterwithin{table}{section}
\counterwithin{figure}{section}

\usepackage{ifthen,version}
\newboolean{include-notes}

% commenting...
 \setboolean{include-notes}{true}
\newcommand{\chrisnote}[1]{\ifthenelse{\boolean{include-notes}}%
 {\textcolor{BrickRed}{\textbf{Chris: #1}}}{}}

% for nice warning symbol
%\usepackage{fourier}

% nice circled numbering
\newcommand*\circled[1]{\tikz[baseline=(char.base)]{
            \node[shape=circle,draw,inner sep=2pt] (char) {#1};}}

\newcommand{\HRule}{\rule{\linewidth}{0.5mm}}
\renewcommand{\thesection}{\thepart \arabic{section}}

\usepackage{pict2e,picture}
\newsavebox\CBox
\newlength\CLength
\def\Circled#1{\sbox\CBox{#1}%
	\ifdim\wd\CBox>\ht\CBox \CLength=\wd\CBox\else\CLength=\ht\CBox\fi
	\makebox[1.2\CLength]{\makebox(0,1.2\CLength){\put(0,0){\circle{1.2\CLength}}}%
	\makebox(0,1.2\CLength){\put(-.5\wd\CBox,0){#1}}}}

\begin{document}

	% Define box and box title style
	\tikzstyle{mybox} = [draw=black, fill=white, thick, rectangle, rounded corners, inner sep=0.4cm]
	\tikzstyle{mytitle} =[fill=black,rectangle, rounded corners, text=white]

	\begin{titlepage}
	\begin{center}
		{ \Large \bfseries How to Create Affordable, Anthropomorphic, Personalized, Light-Weight Prosthetic Hands\\[0.5cm] }
                { \large *George P. Kontoudis, *Minas V. Liarokapis, *Agisilaos G. Zisimatos, *Christoforos I. Mavrogiannis and Kostas J. Kyriakopoulos}

                \vspace{1.4in}

		\fbox{}

                \vspace{1.7in}

		{ \large Technical Report, Control Systems Lab\\
                   School of Mechanical Engineering, National Technical University of Athens \\[0.5cm] }

		{ \large October 2015 $|$ * denotes first author\\[0.5cm]}

	\end{center}
	\end{titlepage}

	\newpage

	\begin{minipage}{0.2\textwidth}
		
	\end{minipage}
	\begin{minipage}{0.8\textwidth}
		\begin{flushleft} \small        
			OpenBionics by \url{www.openbionics.org} is licensed under a  \href{https://creativecommons.org/licenses/by-sa/4.0/}{Creative Commons Attribution-ShareAlike 4.0 International License}.
		\end{flushleft}
	\end{minipage}

	\vspace{12cm}

\begin{center}
 
\end{center}

	{\Large \bfseries Contact: }\\

        \noindent George P. Kontoudis, Agisilaos G. Zisimatos and Kostas J. Kyriakopoulos are with the Control Systems Lab, School of Mechanical Engineering, National Technical University of Athens, 9 Heroon Polytechniou Str, Athens, 15780, Greece (email:\{mc11681,el08087,kkyria\}@mail.ntua.gr).\\

        \noindent Minas V. Liarokapis is with the Dept. of Mechanical Engineering and Materials Science, School of Engineering and Applied Science, Yale University, 9 Hillhouse Avenue, New Haven, CT, 06520, USA (email:minas.liarokapis@yale.edu).\\

        \noindent Christoforos I. Mavrogiannis is with the Sibley School of Mechanical \& Aerospace Engineering, Cornell University, Ithaca, NY, 14853, USA (email:cm694@cornell.edu).\\

	\noindent For any inquiry and/or suggestion you may contact: info@openbionics.org 

\newpage
\tableofcontents
\newpage
\include{Description}

%%%% Appendices %%%% 

\include{Appendix1}
\include{Appendix2}
\include{Appendix3}
\include{Appendix4}

%%%% Bibliography %%%%

\bibliographystyle{ieeetr} 
\bibliography{Ref}

\end{document}

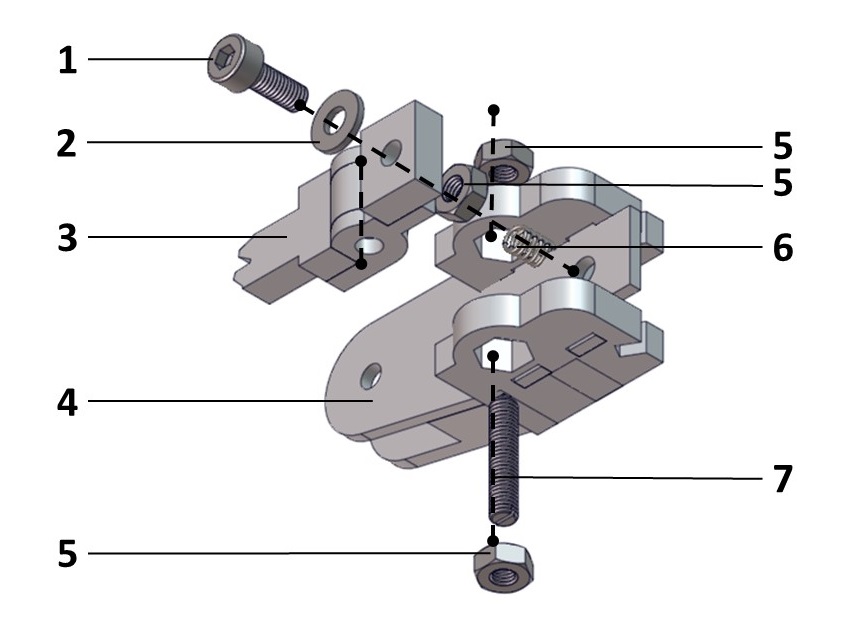
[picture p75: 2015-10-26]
Assembly Guide/tex/figures/Hand/thumbMovingMechansim_lockingMechanism.jpg

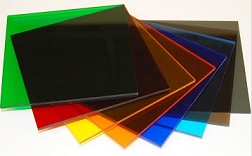
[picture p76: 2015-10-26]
Assembly Guide/tex/figures/Tools/Plexiglas.jpg

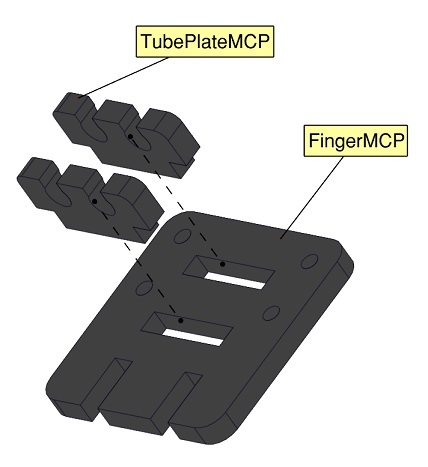
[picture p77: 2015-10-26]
Assembly Guide/tex/figures/Finger/Finger3.jpg

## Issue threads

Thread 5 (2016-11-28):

### ISSUE TITLE
Components to build the prosthetic hands

### ISSUE THREAD

**Issue by jokla** [OpenBionics/Prosthetic-Hands#5]
Hi!

I am looking for the components to buy (I am in France now). 

I would have some questions:
1) Is [this list](https://hackaday.io/project/4745/components) updated?
2) About the [Prosthetic board](https://github.com/OpenBionics/Prosthetic-Hands/tree/master/Electronics). I don't have experience with PCB. Is it possible to buy it somewhere? Otherwise, could you give me some tips to build it?
3) About the Surface electromyography sensing kit: is the new [MyoWare Muscle Sensor](http://www.exp-tech.de/myoware-muscle-sensor) working ? or is it necessary to buy the [old version](http://www.exp-tech.de/sparkfun-ad8232-single-lead-heart-rate-monitor)?
4) Are this [Arduino micro ](http://www.exp-tech.de/arduino-micro) and [this motor](http://www.francerobotique.com/servomoteurs-intelligents/176-herkulex-drs-0201.html) ok? 

Thank you very much in advance!

**Comment by gkontoudis** [comment]
Hello,

Thank you for your interest in our prosthetic hands.

1. Yes it is, but you can use any servo motor and any micro-controller works best for you. You can also check our [Assembly Guide](https://github.com/OpenBionics/Prosthetic-Hands/blob/master/Assembly%20Guide/tex/OpenBionics_ProstheticHandsGuide2015.pdf).
2. The files that you need in order to build the PCB are provided on this [page](https://github.com/OpenBionics/Prosthetic-Hands/tree/master/Electronics). If you face any difficulties, you could skip the PCB building and control the hand directly with the micro-controller. You can find many ways to implement it with respect to the servo motor you plan to use.
3. All versions are working properly, but I suggest you the new version which I also use.
4. You can choose any servo motor and any micro-controller you want.

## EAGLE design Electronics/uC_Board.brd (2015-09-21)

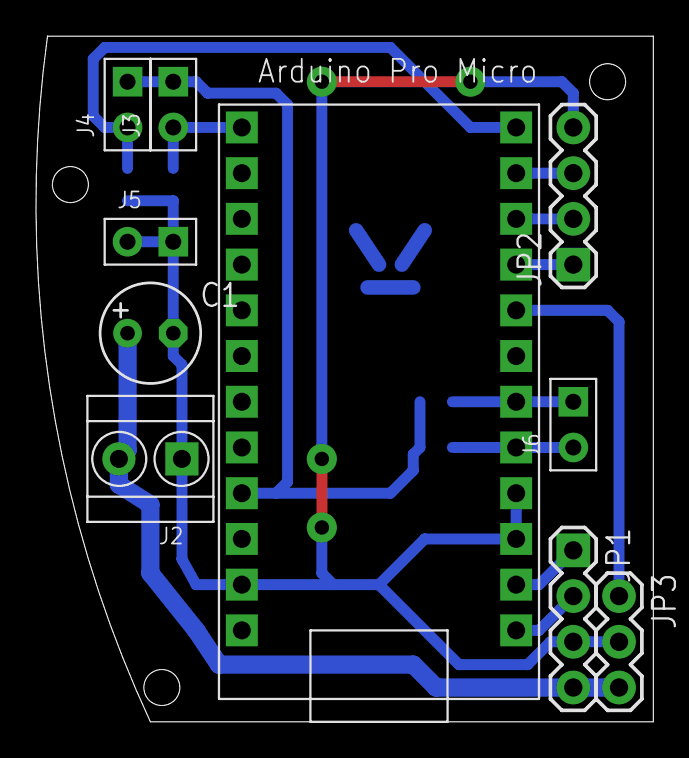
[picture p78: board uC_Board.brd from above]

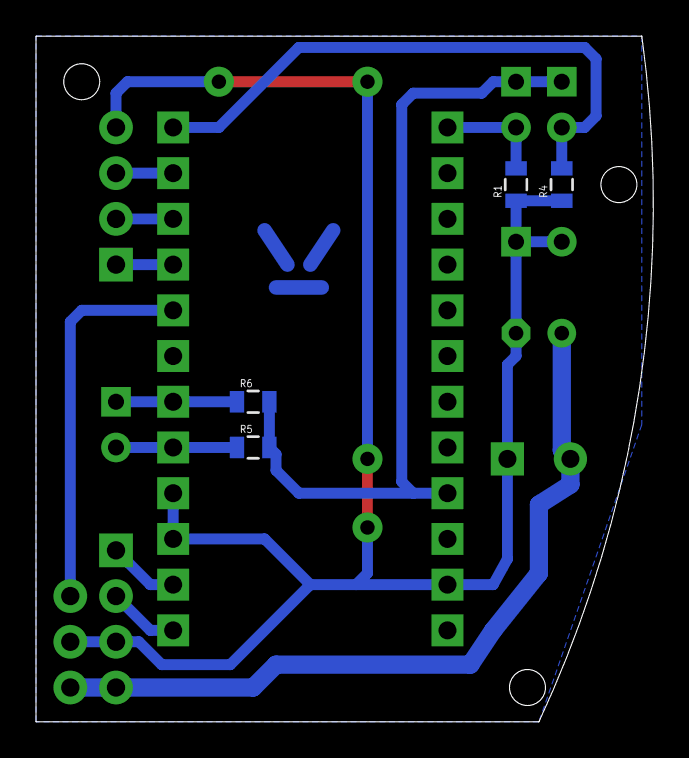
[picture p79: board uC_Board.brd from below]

Board: 2 copper layers, 34.3 x 38.1 mm, 14 parts (4 on the bottom side), 13 nets.

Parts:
ARDUINO_MICRO: ARDUINO_PRO_MICROARDUINO_BOARD; ARDUINO_MICRO_PRO
C1: 100u; E2,5-6
J2: SCREW-TERMINAL-2P-3470070P1; 2P-3.5
J3, J5, J6: 2; 2P-2.54-65/35MIL
J4: 3; 2P-2.54-65/35MIL
JP1, JP2: 1X04
JP3: 1X03
R1, R4: 10k; 0805
R5, R6: 0805

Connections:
A7: ARDUINO_MICRO.10, JP2.2
BUTTON1: ARDUINO_MICRO.13, J3.2, R1.2
BUTTON2: ARDUINO_MICRO.12, J4.2, R4.2
GND: ARDUINO_MICRO.3, ARDUINO_MICRO.4, ARDUINO_MICRO.23, C1.-, J2.1, J5.1, J5.2, JP1.3, JP2.4, JP3.2, R1.1, R4.1
IO1: ARDUINO_MICRO.8, JP3.1
IO2: ARDUINO_MICRO.9, JP2.1
IO3: ARDUINO_MICRO.11, JP2.3
RX: ARDUINO_MICRO.2, JP1.1
SCL: ARDUINO_MICRO.6, J6.1, R6.1
SDA: ARDUINO_MICRO.5, J6.2, R5.1
TX: ARDUINO_MICRO.1, JP1.2
VCC: ARDUINO_MICRO.21, J3.1, J4.1, R5.2, R6.2
VS: C1.+, J2.2, JP1.4, JP3.3

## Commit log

2015-03-20 Add new CAD files
    [AnthropomorphicHandAssembly.SLDASM, BasePulleyInsidePalm.SLDPRT, BasePulleyInsidePalm.STL, BasePulleyInsidePalm2.SLDPRT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]
2015-05-28 Update Assembly
    Resolve conflicts with parameter Finger Width & Palm Radius
    [AnthropomorphicHandAssembly.SLDASM]
2015-05-28 Add Equation to driverBaseFrame
    Equation for change parameter fingerWidth
    [driverBaseFrame1.SLDPRT, driverBaseFrame1.STL]
2015-05-28 Upadate palm to resolve fingerWidth conflicts
    Resolve fingerWidth conflicts, add equation to driverBaseFrame &
    matching of radius
    [palmDown.SLDPRT, palmDown.STL, palmUp.SLDPRT, palmUp.STL]
2015-08-15 Add Left & Right Hand
    Left hand was exist.
    [AnthropomorphicHandAssembly.SLDASM, BasePulleyInsidePalm.SLDPRT, BasePulleyInsidePalm.STL, BasePulleyInsidePalm2.SLDPRT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]
2015-09-21 Add pictures for new prosthetic board.
2015-09-21 Add eagle files for prosthetic hand board.
    [uC_Board.brd, uC_Board.sch]
2015-09-21 Add firmware for arduino and library for Herkulex DRS-0201.
2015-09-21 Add example for arduino micro and library for Herkulex servo.
2015-09-21 Add freecad files for palmup-down parts and pictures for these.
    [PalmDown.fcstd, PalmUp.fcstd]
2015-10-24 Update and add new palm parts.
    [BarIndexMiddle.fcstd, BarIndexMiddle.stl, BarRingPinky.fcstd, BarRingPinky.stl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]
2015-10-24 Add new thumb part.
    [ThumbBase.fcstd, ThumbBase.stl]
2015-10-24 Add new custom flange part.
    [CustomFlange.fcstd]
2015-10-24 Add parts for buttons.
    [Button.STL, Button.fcstd, ButtonAxle.fcstd, ButtonBase.fcstd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]
2015-10-24 Add 3D Design
    [AnthropomorphicHandAssembly.SLDASM, BasePulleyInsidePalm.SLDPRT, BasePulleyInsidePalm.STL, BasePulleyInsidePalm2.SLDPRT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]
2015-10-24 Update button parts.
    [BarIndexMiddle.fcstd, Button.fcstd, ButtonFrame.fcstd, buttonAxle.STL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]
2015-10-24 Temporarily Delete
    [AnthropomorphicHandAssembly.SLDASM, BasePulleyInsidePalm.SLDPRT, BasePulleyInsidePalm.STL, BasePulleyInsidePalm2.SLDPRT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]
2015-10-24 Same button with 2D Design
    Rendered
    [Button.SLDASM, ButtonAssembly.STL, buttonAxle.SLDPRT, buttonAxle.STL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]
2015-10-24 Update fingers with bridges
    [commonFingersTube.SLDPRT, driverBaseFrame1.SLDPRT, driverBaseFrame2.SLDPRT, index.SLDASM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]
2015-10-24 Update Flange for different interfaces
    New fixing type with palm
    [FlangeCoupling.SLDASM, FlangeCoupling.STL, FlangePlate.SLDPRT, FlangePlate.STL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]
2015-10-24 Update palm for 3d Printing
    [palmDown.SLDASM, palmDown.SLDPRT, palmDown.STL, palmUp.SLDASM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]
2015-10-24 Add assembly stages
    [palmDown_toothedMechanism.SLDASM, palmDown_toothedMechanismAssembled.SLDASM, palmTendonRouting_support.SLDASM, palmUpComplete_Whiffletree.SLDASM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]
2015-10-24 Fix parametering bugs
    [prostheticParameters.SLDPRT]
2015-10-24 Add new servo base and pulley for Hekrulex DRS 201
    [SupportPulleyPalmUpAssem.SLDASM, SupportPulleyPalmUpAssem.STL, baseHerkulex.SLDPRT, baseHerkulex.STL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]
2015-10-24 Add 3d printed thumb and different stages of assembly
    [lockMechanismBracket.SLDPRT, lockMechanismBracket.STL, lockMechanismSupport.SLDPRT, lockMechanismSupport.STL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]
2015-10-24 Same design with 2D
    [BasePulleyInsidePalm.SLDPRT, BasePulleyInsidePalm.STL, BasePulleyInsidePalm2.SLDPRT, BasePulleyInsidePalm2.STL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]
2015-10-24 3d printed assembly
    Fully Rendered
    [AnthropomorphicHandAssembly.SLDASM]
2015-10-25 Add body harness sources and readme file.
    [BackCross.SLDPRT, HarnessEE.SLDPRT, HarnessEE.STL, HarnessEntry.SLDPRT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]
2015-10-26 Add source files and stl for HDM design.
    [Base.STL, Base.sldprt, IndexMold-Both.SLDPRT, IndexMold-Left.STL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]
2015-10-26 Add missing stl and source files to HDM design.
    [palm.STL, thumbLockingMechanism.SLDPRT, thumbLockingMechanism.STL, thumbMechanism.SLDPRT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]
2015-10-26 Add Readme for 3D printed parts
2015-10-26 Add Readme for Laser Cutting files
2015-10-26 Move files
    [BasePulleyInsidePalm.STL, FlangePlate.STL, SupportPulleyPalmUpAssem.STL, barIndexMiddle.STL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]
2015-10-26 Update laser Readme
2015-10-26 Add Assembly guide and update .gitignore. We couldn't resolved the conflict with 3dPrinted branch.
2016-10-27 Rearranged files for Left hand
    [AnthropomorphicHandAssembly.SLDASM, BasePulleyInsidePalm.SLDPRT, BasePulleyInsidePalm.STL, BasePulleyInsidePalm2.SLDPRT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]
2016-10-27 Add right hand
    [barIndexMiddle.SLDPRT, barIndexMiddle.STL, barRingPinky.SLDPRT, barRingPinky.STL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]
2016-11-05 Added equations so as to take into account the tolerances of different 3D Printers
    [prostheticParameters.SLDPRT]
2016-11-05 Added equations to some parts so as to take into account the tolerances of different 3D Printers
    [BasePulleyInsidePalm.SLDPRT, BasePulleyInsidePalm.STL, BasePulleyInsidePalm2.SLDPRT, Button.SLDASM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]
2016-11-23 Add tube driver
    [tubeDriver.STL]
2016-11-25 Remove old 3D printed files
    [BasePulleyInsidePalm.STL, FlangePlate.STL, SupportPulleyPalmUpAssem.STL, barIndexMiddle.STL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]
2016-11-25 Add new 3D printed files for left hand
    [BasePulleyInsidePalm.STL, FlangePlate.STL, SupportPulleyPalmUpAssem.STL, barIndexMiddle.STL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]
2016-11-25 Add new 3D printed files for right hand
    [SupportPulleyPalmUpAssem.STL, barIndexMiddle.STL, barRingPinky.STL, baseHerkulex.STL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]
2017-05-11 Fix bug in right hand
    [barIndexMiddle.SLDPRT, barRingPinky.SLDPRT, basePulleyInsidePalm.SLDPRT, button.SLDASM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]
2017-05-11 Fix bug in left hand
    [AnthropomorphicHandAssembly.SLDASM, BasePulleyInsidePalm.SLDPRT, BasePulleyInsidePalm2.SLDPRT, Button.SLDASM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]

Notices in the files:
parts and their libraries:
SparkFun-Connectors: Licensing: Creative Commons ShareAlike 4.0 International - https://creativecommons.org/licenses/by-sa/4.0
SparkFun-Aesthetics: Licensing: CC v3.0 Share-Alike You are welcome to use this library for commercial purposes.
